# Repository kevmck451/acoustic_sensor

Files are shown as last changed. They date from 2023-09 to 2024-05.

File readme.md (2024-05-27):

# Acoustic Sensor
	- University of Memphis
	- Multiple Unmanned Ariel System Project
	- Army Research Lab

The audio recording device used in the experiment was the Sony Spresense microcontroller with custom firmware developed to enable recording across four analog channels at a 16-bit resolution and a 48 kHz sampling rate. We utilized the CMI-5247TF-K10 electret condenser microphone, recommended by Spresense documentation for its compatibility and straightforward setup with the microcontroller. This unidirectional microphone has an operational frequency range of 70 Hz to 20 kHz. Additionally, a shield circuit was designed for the microcontroller to integrate microphone inputs, potentiometers for calibrating microphone levels, an OLED display screen, and sensors for temperature, humidity, and pressure. The device’s enclosure and microphone mount were designed using CAD software and produced via 3D printing. For wind noise mitigation, the microphones were equipped with dual layers of wind protection: an initial layer consisting of thin foam covers typical for lavalier microphones, followed by wind muffs also designed for lavalier microphones. While this setup effectively reduces wind noise for winds up to 5 m/s, there remains considerable scope for enhancing physical wind noise reduction techniques.

## Read Manual.md for specific instructions on data collection

## Acoustic_Firmware
	- firmware and header files for arduino IDE upload
	- Acoustic_Firmware.ino
	- screen.h
	- temp.h

## BIN
	- this needs to be on the sony spresense formated SD card
	- includes the audio codecs used for recording
	- gain.txt file to store the default gain setting

## Docs
	- Recorder Schematic
	- Parts List
	- Recorder Versions
	- Sony Microcontroller Notes

## Enclosure
	- 3D Printer Enclosure files
	- MicModuleBoxrev3.data
	- MicModuleBoxrev3.gcode

## Shield
	- Sony Spresense Shield KiCad File
	- Mic Resisters: 2.2k Ohms
	- Capacitors: 1uF
	- Potentiometers: 500k Ohms

# Acoustic Sensor
Acoustic Sensor
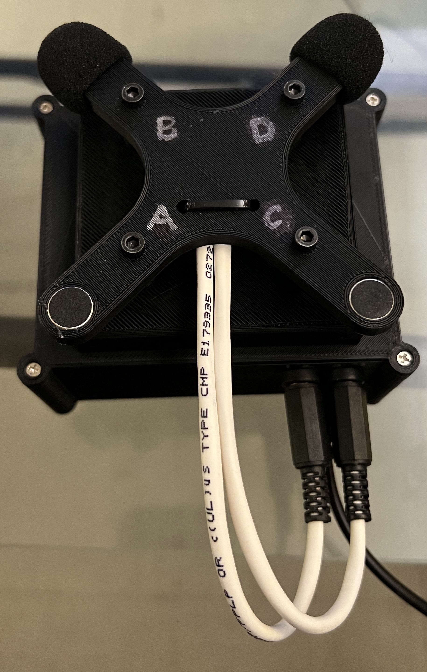
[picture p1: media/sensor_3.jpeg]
Acoustic Sensor


# KiCad Model
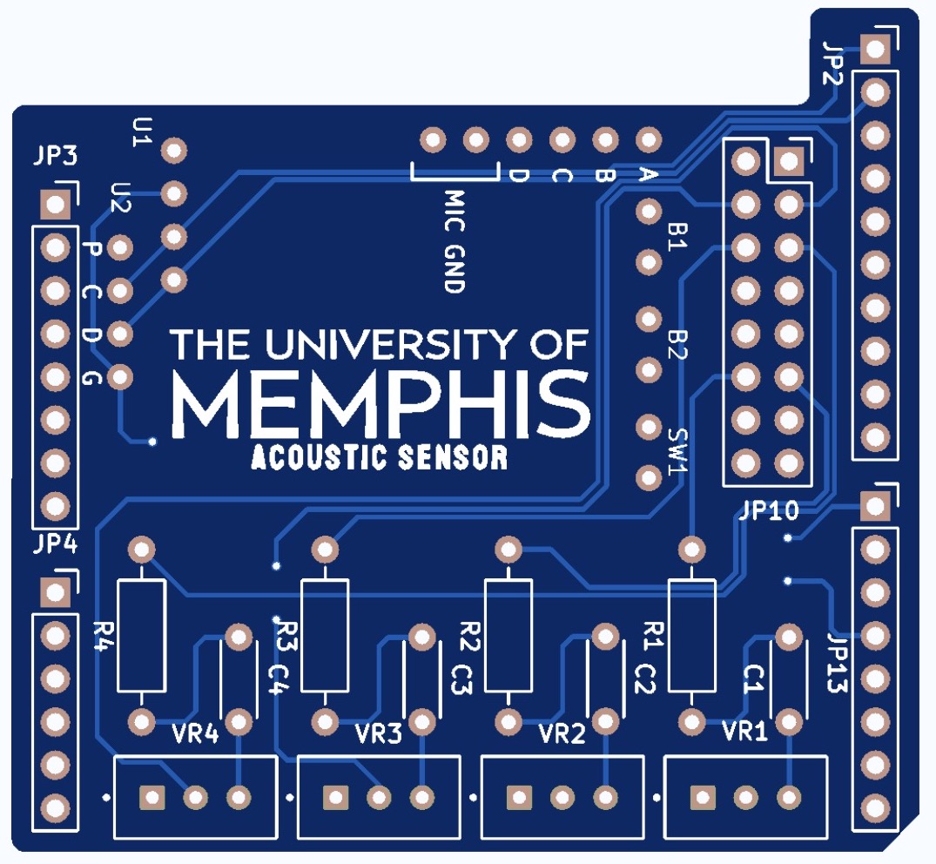
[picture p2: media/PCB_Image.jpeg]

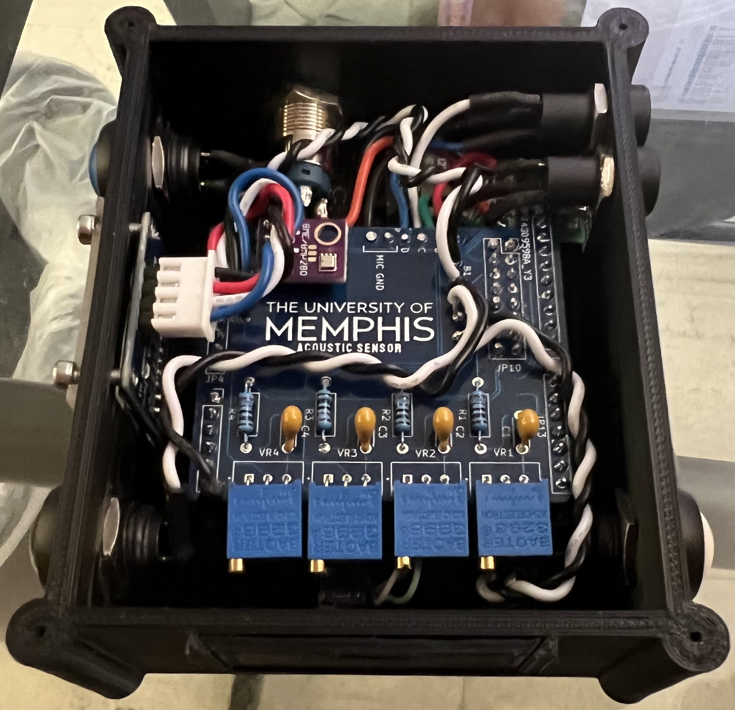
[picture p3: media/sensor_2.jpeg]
Acoustic Sensor


# In Action
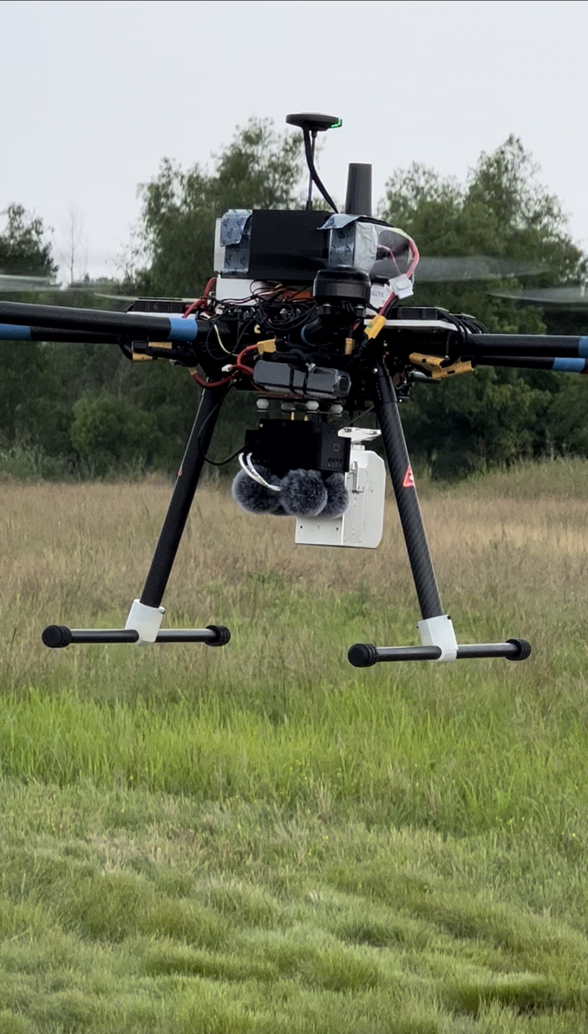
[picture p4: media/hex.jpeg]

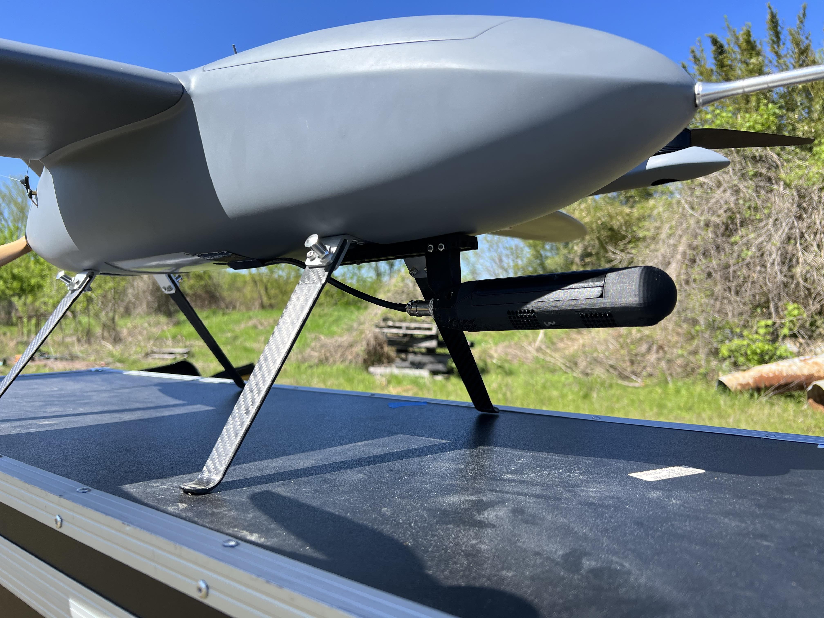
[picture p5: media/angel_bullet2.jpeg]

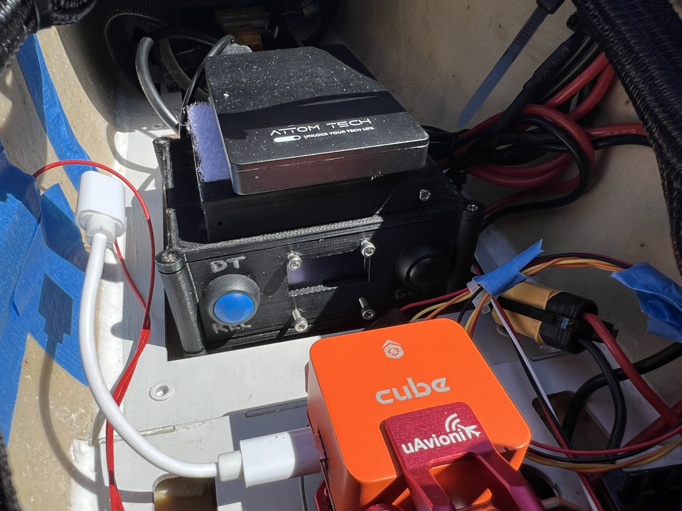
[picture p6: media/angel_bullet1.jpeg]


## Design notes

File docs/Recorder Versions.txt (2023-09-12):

Acoustic Recorder Versions

Version 4: 9/11/23
	- Include gain setting on stand by screen
	- Retrieve gain setting from text file saved on SD card
	- Cycle through gain settings in increments of 2dB
	- Save current gain setting as default (overwrite setting in file)
	- If gain button is pressed during recording, current record time is displayed
	- Increased bit depth to from 16 to 24 bit
	- Temp / Humid / Pressure pre / post recording is averaged to get 1 value for each
	- Switch could be where screen flashes before starting record so you can sync to external timer

Version 3_2: 5/5/23
	- Same as V3.1 but with mods to avoid noise during recordings
	- Temp / Humid / Pressure logged once before recording and once after
	- Recording Time: 60mins
	- Gain increased from to 100 (+10dB) to 160 (+16dB)

Version 3_1: 5/3/23
	- Modes: Stand By / Data Transfer / Recorder
	- 4 Channel / 48kHz Sample Rate
	- 16 bit depth
	- Metadata logs in csv files 2Hz
	- Updated screens
	- Temperature offset for calibration
	- Humidity offset for calibration
	- Screen & Temp sensor cause noise in recordings
	- They are sampled during recordings

Version 3: 4/25/23
	- Modes: Standby / Recorder
	- 4 Channel / 48k SR
	- 24 bit depth
	- OLED Screen
	- Temp / Humid/ Pressure Sensor
	- SD Access from extension board

Version 2_2: 4/18/23
	- Modes: Throughput / Recorder
	- 1 Channel / 192k Sample Rate
	- 24 bit depth
	- Increase Memory (1024)
	- Specific Buffer Size

Version 2_1: 3/25/23
	- Modes: Throughput / Recorder
	- 48k Sample Rate
	- Software Gain: 200
	- Stop Recording Bug

Version 2: 3/5/23
	- Modes: Throughput / Recorder
	- 2 Channel

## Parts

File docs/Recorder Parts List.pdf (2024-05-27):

Acoustic Recorder Parts List

3.5MM Audio Jack Socket Connector Headphone Jack Connector 3 Pole Black with Nut

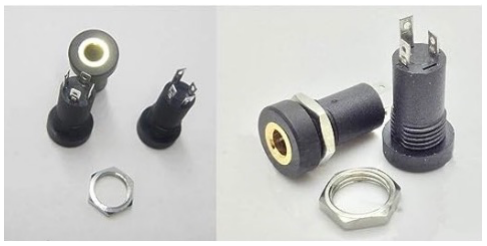
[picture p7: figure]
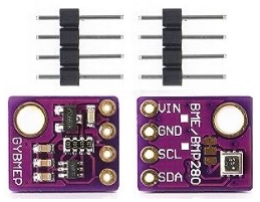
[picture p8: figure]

BME280 5V Temperature Humidity Sensor Atmospheric Barometric Pressure Sensor with IIC I2C Breakout

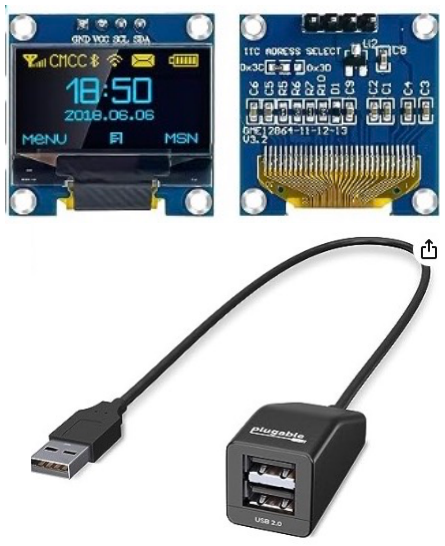
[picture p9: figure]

0.96 Inch OLED I2C IIC Display Module 12864 128x64 Pixel SSD1306 Mini Self-Luminous OLED Screen Board

Plugable 2-in-1 USB Splitter with Dual USB 2.0 Ports, Driverless Compatibility for Windows, Linux, macOS, Chrome OS, USB Multiport Hub for Laptops

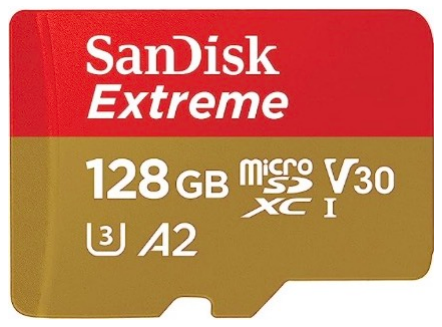
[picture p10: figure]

SanDisk 128GB Extreme microSDXC UHS-I Memory Card

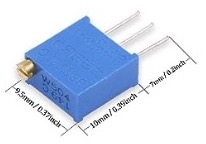
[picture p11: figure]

500K ohm 3296W Multiturn Trimmer Potentiometer

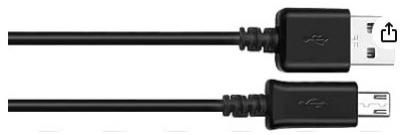
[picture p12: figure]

Micro USB Cable 3.3 ft, Data Micro USB to USB A Cord

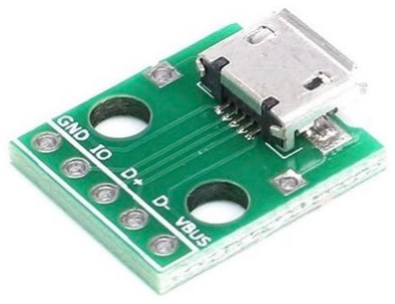
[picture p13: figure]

Micro USB to DIP Adapter 5pin Female Connector B Type PCB Converter pinboard

SPST 2 Position On/Off 2 Pin Mini Boat Rocker Switch

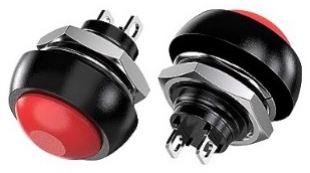
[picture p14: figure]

Momentary Push Button Switch 12MM Normal Open(NO) Mini Micro Switch ON-Off


12mm Latching led Push Button Switch Silver Shell with pre-Wiring


TRS Male Plug 3 Pole 1/8" 3.5mm Solder Type DIY Audio Cable Connector

M2.5 Male Female Hex Brass Spacer Standoff Screw Nut Assortment Kit

2.2K ohm Resistor 1/4w (0.25 Watt) ±1% Tolerance Metal Film Fixed Resistor

Cubilux Furry Windscreen & Foam Cover Set for Lavalier Lapel Microphone, Wind Muff & Dead Cat Set for Mini Clip-On Lav MIC

Attom Tech Dual USB Output Super Slim Power Bank Ultra Thin, 3000mAh Portable Charger Mini External Phone Battery Pack


Monolithic Ceramic Capacitor Assortment kit 10pf－10uF

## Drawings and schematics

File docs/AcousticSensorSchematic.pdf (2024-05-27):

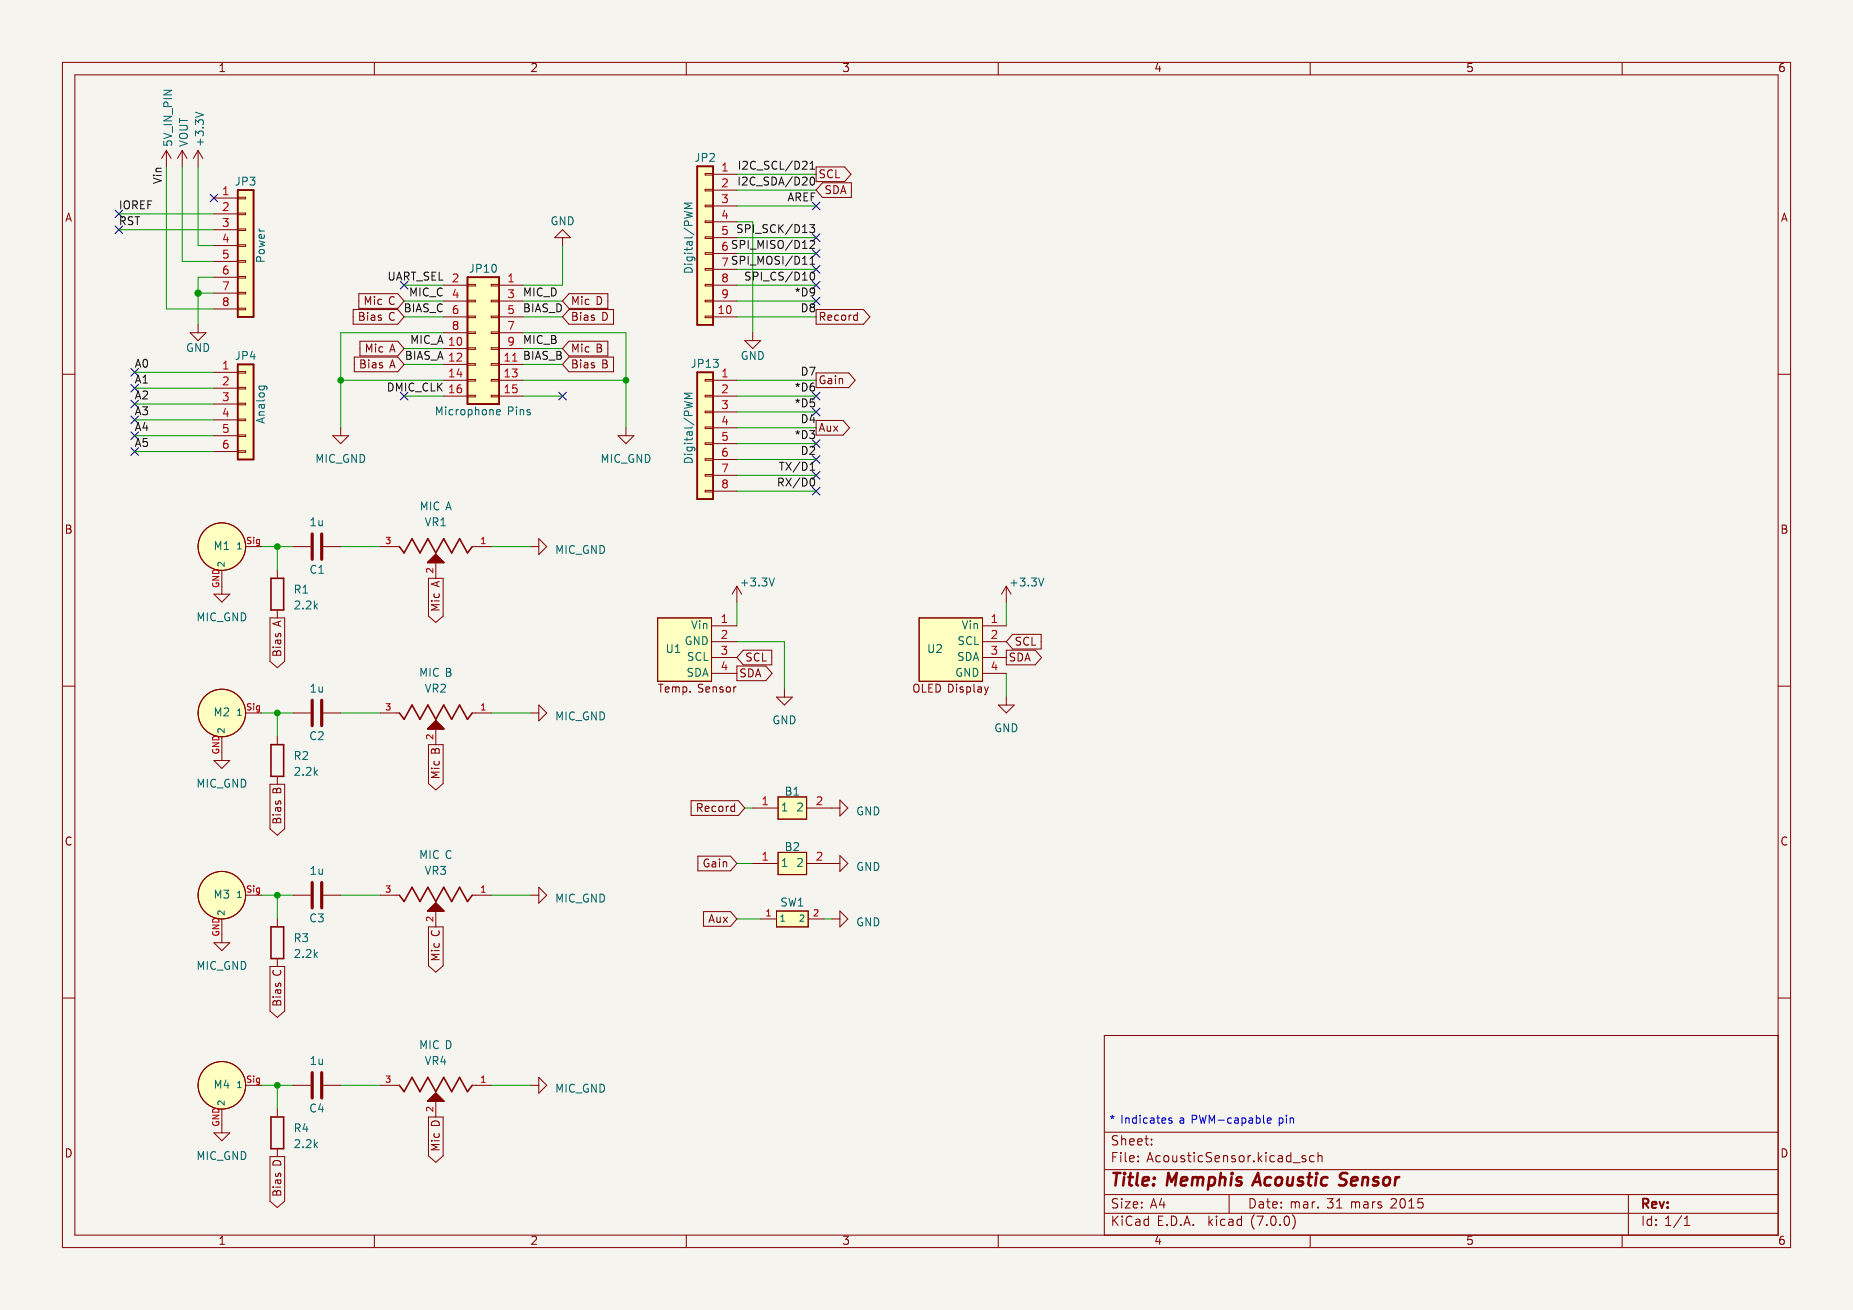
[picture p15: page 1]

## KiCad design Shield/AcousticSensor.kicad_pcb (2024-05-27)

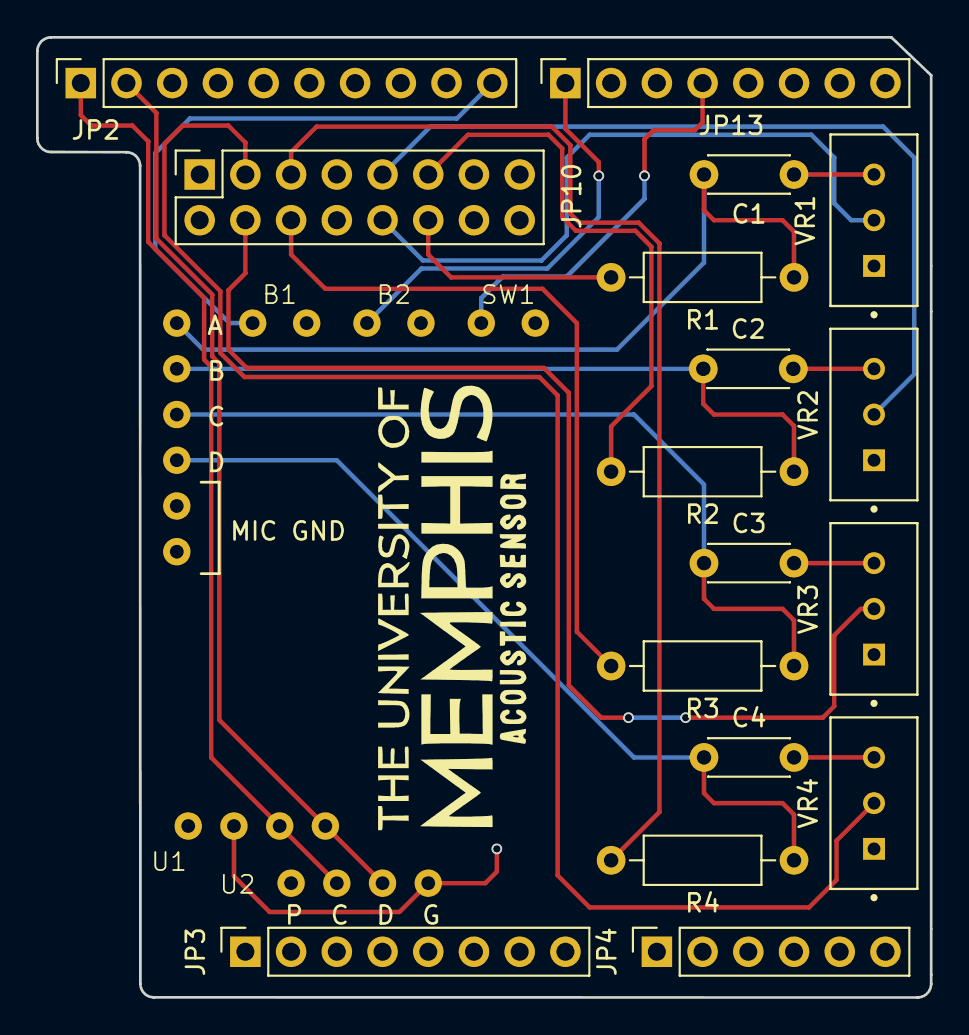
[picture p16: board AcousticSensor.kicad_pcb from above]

Board: 4 copper layers, 49.7 x 53.3 mm, 22 parts (0 on the bottom side), 24 nets.

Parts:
B1, B2: Jumper-Cable_Button-Switch
C1, C2, C3, C4: 1u; C_Disc_D4.3mm_W1.9mm_P5.00mm
JP2: Digital/PWM; PinSocket_1x10_P2.54mm_Vertical
JP3: Power; PinSocket_1x08_P2.54mm_Vertical
JP4: Analog; PinSocket_1x06_P2.54mm_Vertical
JP10: Microphone Pins; PinSocket_2x08_P2.54mm_Vertical
JP13: Digital/PWM; PinSocket_1x08_P2.54mm_Vertical
R1, R2, R3, R4: 2.2k; R_Axial_DIN0207_L6.3mm_D2.5mm_P10.16mm_Horizontal
SW1: Jumper-Cable_Button-Switch
U1, U2: OLED_Display
VR1: MIC A; TRIM_3296W-1-103
VR2: MIC B; TRIM_3296W-1-103
VR3: MIC C; TRIM_3296W-1-103
VR4: MIC D; TRIM_3296W-1-103

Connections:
+3V3: JP3.4, U1.1 (Vin), U2.1 (Vin)
Aux: JP13.4, SW1.1
Bias A: JP10.12, R1.2
Bias B: JP10.11, R2.2
Bias C: JP10.6, R3.2
Bias D: JP10.5, R4.2
GND: B1.2, B2.2, JP2.4, JP3.6, JP3.7, JP10.1, SW1.2, U1.2 (GND), U2.4 (GND), VR1.1, VR2.1, VR3.1, VR4.1
GNDA: JP10.7, JP10.8, JP10.13, JP10.14
Gain: B2.1, JP13.1
Mic A: JP10.10, VR1.2
Mic B: JP10.9, VR2.2
Mic C: JP10.4, VR3.2
Mic D: JP10.3, VR4.2
unnamed: C1.1, VR1.3
unnamed: C2.2, VR2.3
unnamed: C3.2, VR3.3
unnamed: C4.2, VR4.3
unnamed: C1.2, R1.1
unnamed: C2.1, R2.1
unnamed: C3.1, R3.1
unnamed: C4.1, R4.1
Record: B1.1, JP2.10
SCL: JP2.1, U1.3 (SCL), U2.2 (SCL)
SDA: JP2.2, U1.4 (SDA), U2.3 (SDA)

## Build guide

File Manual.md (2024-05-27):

# Acoustic Sensor Manual
for Angel UAV and Bullet2 Mic Mount

### Parts:
	- recorder
	- battery with cable
	- bullet2 mic mount
	- mic cable
	- data cable

### Physical Setup:
	- slide bullet2 onto front of angel's mount
	- screw both hex bolts through to secure
	- place recorder inside angel (should be velcro to hold in place)
		- battery should be already attached and charged
	- plug in mic cable to bullet and recorder and screw in
	- recomended to tape down mic cable at entry to body of angel

### Data Collection:
	- Press latch button on side to turn on (creen will turn on)
	- confirm that the gain setting is at 0dB (should be default)
		- if not at 0, press right button (black) until at correct number
	- once ready to start recording, press left button (blue)
		- screen should change to indicate recording has started
	- when done, press left button (blue) again
		- screen should change to indicate recording has ended
	- to start another recording, turn device on and back on and repeat process again

### Data Retrieval:
	- using the micro usb cable, plug into device and into computer
	- press and hold the left button (blue), then power on device with latch button
	- continue to hold blue button until the Data Transfer Screen appears
	- this will mount a device on your computer to get files
		- device uses usb2.0 so it's slow, be patient
	- when finished, eject mounted device from computer
	- when device has left your computer, you can turn it off

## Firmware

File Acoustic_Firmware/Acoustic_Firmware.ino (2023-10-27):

/* University of Memphis Acoustic Sensing */ 
/* Audio Recorder for MUAS Project */
/* Kevin McKenzie - 2023 */

/* Included Libraries */
    #include <arch/board/board.h>
    #include <Arduino.h>
    #include <SDHCI.h>
    #include <Audio.h>
    #include <string>
    #include <sstream>
    #include <iostream>
    #include "screen.h"
    #include "temp.h"


/* Global Variables */
    String PROGRAM_NAME = "Acoustic Main V4.0 - 9/12/23-Kevin McKenzie";
    bool first_time = true;
    static const int ButtonPin = 8;
    static const int GainPin = 7;
    static const int resetPin = 13;
    unsigned long sample_millis = millis();
    float samptime = 1.0;  //0.9158

/* Screen */
    int error_thrown = false;
    String error_type = "";

/* SD Card */
    SDClass theSD;
    File myFile;
    #define FILENAME_LENGTH 23  
    String RECORD_FILE_NAME;
    int fileNumber;
    String file_time = "00:00";
    String old_file_time = "00:00";
    bool data_transfer_mode = false;

/* Temp Sensor */
    Adafruit_BME280 bme;
    int temp = 0;
    int humid = 0;
    int pressure = 0;

/* Audio */
    AudioClass *theAudio;
    bool ErrEnd = false;
    bool recording_in_progress;

    static const uint32_t recoding_sampling_rate = 48000;  
    static const uint8_t recoding_channel_number = 4;
    static const uint8_t recoding_bit_length = 16;  
    static const uint32_t recoding_time = 3600;     // 1800 seconds is 30min
    static const int32_t recoding_byte_per_second = recoding_sampling_rate * recoding_channel_number * recoding_bit_length / 8;
    static const uint64_t recoding_size = recoding_byte_per_second * recoding_time;
    static const uint32_t buff_size = 500 * 1024;  // default = 160k
    bool gain_button_pressed = false;
    bool gain_button_released = false;
    int recording_second_1 = 0;
    int recording_second_2 = 0;
    int recording_minute_1 = 0;
    int recording_minute_2 = 0;
    int gain_value = 0;


//----------------------------------------------------------------------------
//-------------- SETUUUUUUP --------------------------------------------------
//----------------------------------------------------------------------------
void setup() {
    /* Setup */
      Serial.begin(115200);
      Serial.println(PROGRAM_NAME);

      pinMode(LED0, OUTPUT);
      pinMode(LED1, OUTPUT);
      pinMode(LED2, OUTPUT);
      pinMode(LED3, OUTPUT);
      pinMode(ButtonPin, INPUT_PULLUP); // Recording & Data Transfer Mode Button
      pinMode(GainPin, INPUT_PULLUP); // Gain Level & Auxiliary Function Button
      pinMode(resetPin, OUTPUT); // To Reset Board

    /* Data Transfer Mode */
      if (!digitalRead(ButtonPin)) {
        delay(1000);
        if (!digitalRead(ButtonPin)) {
            data_transfer_mode = true;        
          }
        }

    /* Screen */
      if(!display.begin(SSD1306_SWITCHCAPVCC, SCREEN_ADDRESS)) {
          Serial.println("Screen Not Found");
          for(;;); // Don't proceed, loop forever
          }

      display.clearDisplay(); // Clear the buffer
      delay(1000); // Pause for 2 seconds
      drawBM(bitmap_title);
      delay(3000);

    /* SD Card */
      while (!theSD.begin()) {
          /* wait until SD card is mounted. */
          if (first_time) {Serial.println("Insert SD card"); first_time = false;}
          String text = "Insert SD Card";
          error_type = "No SD Card";
          error_thrown = true;
          display.clearDisplay(); // Clear the buffer
          delay(1000); // Pause for 2 seconds
          drawScreen_Error(temp, humid, pressure, text.c_str(), error_type.c_str(), file_time.c_str());
          insertSDLEDS();
          }
      if (data_transfer_mode) {
        delay(1000);
        theSD.beginUsbMsc(); 
        drawScreen_DT();
        while(true) {}
        }
      if (error_thrown) {
        Serial.println("SD Card Entered");
        error_thrown = false;
        first_time = true;
        delay(100);
        }
  
    /* Temp Sensor */
      if (!bme.begin(0x76)) {
          display.clearDisplay(); // Clear the buffer
          delay(1000); // Pause for 2 seconds
          drawScreen_TempError();
          if (first_time) {
            Serial.println("Temp Sensor Not Found"); 
            Serial.println("Restart Device");
            first_time = false;
            }
          error_thrown = true;
          
          while (digitalRead(ButtonPin)) {
            insertSDLEDS();
            }
        } // if
      if (error_thrown) {
        Serial.println("Continuing without Temp Sensor");
        first_time = true;
        error_thrown = false;
        delay(1000);
        } // if

      temp = temp_sensor(bme);
      humid = humid_sensor(bme);
      pressure = press_sensor(bme);

    /* Stand By */
      Serial.println("Standing By");
      Serial.println("Press Button to Start Recording");
      unsigned long sb_current_millis = millis(); 
      int sbst = samptime * 1000;
      uint32_t mic_gain = readGain();
      unsigned long gain_millis;
      
      
      while (digitalRead(ButtonPin)) {
          bool default_set = false;
          int gain = mic_gain / 10;
          gain_value = gain;
          temp = temp_sensor(bme);
          humid = humid_sensor(bme);
          pressure = press_sensor(bme);
          drawScreen_Standby(temp, humid, pressure, gain); 

          if (!digitalRead(GainPin)) {
            gain_millis = millis();

            while (!digitalRead(GainPin)) {
              unsigned long current_millis = millis();

              if (current_millis - gain_millis > 5000) {
                setGainDefault(gain);
                drawScreen_GainDefault(gain);
                Serial.println("New Default Set!");
                default_set = true;
                delay(3000);
                break;
                } // if
              } // while

            if (!default_set) {
              if (mic_gain > 210) { mic_gain = 0;}
              else {mic_gain += 20;} 
            } // if 
          } // if button
        } // while stand by

    /* Audio */
      // Initialize
        theAudio = AudioClass::getInstance();
        theAudio->begin(audio_attention_cb);
        // theAudio->setRenderingClockMode(AS_CLKMODE_HIRES); 
        theAudio->setRecorderMode(AS_SETRECDR_STS_INPUTDEVICE_MIC, mic_gain, buff_size); 
        theAudio->initRecorder(AS_CODECTYPE_WAV,
                           "/mnt/sd0/BIN",
                           recoding_sampling_rate,
                           recoding_bit_length,
                           recoding_channel_number);

    /* File */
      fileNumber = 1;
      String record_filename = String(fileNumber) + ".wav";
      RECORD_FILE_NAME = record_filename;

      while (theSD.exists(RECORD_FILE_NAME)) {
        fileNumber++;
        record_filename = String(fileNumber) + ".wav";
        RECORD_FILE_NAME = record_filename;
        }

      Serial.print("Filename: ");
      Serial.println(RECORD_FILE_NAME);
      File file = theSD.open(RECORD_FILE_NAME, FILE_WRITE);

      if (!file){
        Serial.println("Error creating file");
        }
        else {
        Serial.println("File created successfully");
        file.close();
        }

      myFile = theSD.open(RECORD_FILE_NAME, FILE_WRITE);

      if (!myFile) {
        printf("File open error\n");
        exit(1);
        } 

    /* Start Recording */
      logData(temp_sensor(bme), humid_sensor(bme), press_sensor(bme));
      Serial.println("Recording Started!");
      recording_in_progress = true;
      lightsON();
      theAudio->writeWavHeader(myFile);
      theAudio->startRecorder();
      drawScreen_Recording(temp, humid, pressure, RECORD_FILE_NAME.c_str(), file_time.c_str(), gain_value);
      

} // setup

//----------------------------------------------------------------------------
//-------------- LOOOOOOOOP --------------------------------------------------
//----------------------------------------------------------------------------
void loop() {
    /* Setup */
      int recording_button = digitalRead(ButtonPin);
      int gain_button = digitalRead(GainPin);
      unsigned long current_millis = millis(); 
      int st = samptime * 1000;
      err_t err;
    
    /* Read frames to record in file */
      err = theAudio->readFrames(myFile);

    /* Screen Timer */
      if ((current_millis - sample_millis) > st) {
          recording_second_1++;
          if (recording_second_1 > 9) {
            recording_second_1 = 0;
            recording_second_2++;
            if (recording_second_2 > 5) {
              recording_second_2 = 0;
              recording_minute_1++;
              if (recording_minute_1 > 9) {
                recording_minute_1 = 0;
                recording_minute_2++;
                if (recording_minute_2 > 5) {
                  recording_minute_2 = 0;
                  }
                }
              }          
            }

          std::stringstream ss;
          ss << recording_minute_2 << recording_minute_1 << ":" << recording_second_2 << recording_second_1;
          std::string time_str = ss.str();
          file_time = ss.str().c_str();
          // drawScreen_Recording_Time(temp, humid, pressure, RECORD_FILE_NAME.c_str(), file_time.c_str());
          // logData(temp_sensor(bme), humid_sensor(bme), press_sensor(bme));
          sample_millis = millis();
          } // if



    /* Update Record Time */
      if (gain_button == 0) {gain_button_pressed = true;}
      if (gain_button_pressed && gain_button == 1) {gain_button_released = true;}
      if (gain_button_pressed) {
        if (old_file_time != file_time.c_str()) {
          drawScreen_Recording_Time(temp, humid, pressure, RECORD_FILE_NAME.c_str(), file_time.c_str(), gain_value);
          Serial.println("Time Updated");
          old_file_time = file_time.c_str();
            }
        } // if

      if (gain_button_released) {
        gain_button_pressed = false;
        gain_button_released = false;
        drawScreen_Recording(temp, humid, pressure, RECORD_FILE_NAME.c_str(), file_time.c_str(), gain_value);
        }


    /* Stop Recording */
      if (recording_in_progress && !recording_button) {
          Serial.println("Recording Button Pressed");
          theAudio->stopRecorder();
          sleep(1);
          err = theAudio->readFrames(myFile);
          drawScreen_Recording_Suc(temp, humid, pressure, RECORD_FILE_NAME.c_str(), file_time.c_str(), gain_value);
          goto exitRecording;
          }

      if (theAudio->getRecordingSize() > recoding_size) {
          theAudio->stopRecorder();
          sleep(1);
          err = theAudio->readFrames(myFile);
          drawScreen_Recording_Suc(temp, humid, pressure, RECORD_FILE_NAME.c_str(), file_time.c_str(), gain_value);
          goto exitRecording;
          }

    /* Errors */
      if (err != AUDIOLIB_ECODE_OK) {
          Serial.printf("File End! =%d\n", err);
          error_thrown = true;
          theAudio->stopRecorder(); 
          Serial.println("Error Area 1");
          error_type = "Error 1";
          drawScreen_Error(temp, humid, pressure, RECORD_FILE_NAME.c_str(), error_type.c_str(), file_time.c_str());
          goto exitRecording;
          }

      if (ErrEnd) {
          Serial.printf("Error End\n");
          error_thrown = true;
          theAudio->stopRecorder(); 
          Serial.println("Error Area 2");
          error_type = "Error 2: FIFO";
          drawScreen_Error(temp, humid, pressure, RECORD_FILE_NAME.c_str(), error_type.c_str(), file_time.c_str());
          goto exitRecording;
          }

      return;
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

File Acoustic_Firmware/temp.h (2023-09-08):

// Code for Sensors of Acoustic Module

#include <Arduino.h>
#include <Adafruit_BME280.h>  // temp/humid sensor
#include <Adafruit_Sensor.h>

// ----- TEMP/HUMID SENSOR
#define SEALEVELPRESSURE_HPA (1013.25) 



// -------------------- FUNCTIONS -----------------------

int temp_sensor(Adafruit_BME280& bme) {
  int offset = -5;
  float temperatureC = bme.readTemperature(); // read temperature from BME280 sensor
  int temperature = temperatureC * 9/5 + 32; // convert to Fahrenheit

  // Serial.print("Temperature: ");
  // Serial.print(temperature);
  // Serial.println(" F");

  return temperature + offset;

}

int humid_sensor(Adafruit_BME280& bme) {
  int offset = 5;
  int humidity = bme.readHumidity(); // read humidity from BME280 sensor

  // Serial.print("Humidity: ");
  // Serial.print(humidity);
  // Serial.println(" %");

  return humidity + offset;

}

int press_sensor(Adafruit_BME280& bme) {
  int pressure = bme.readPressure() / 100.0F; // read pressure from BME280 sensor
  // int pressure = map(pressure, 300, 1100, 0, 100); // map pressure to percentage value

  // Serial.print("Pressure: ");
  // Serial.print(pressure);
  // Serial.println(" hPa");

  return pressure;

}
